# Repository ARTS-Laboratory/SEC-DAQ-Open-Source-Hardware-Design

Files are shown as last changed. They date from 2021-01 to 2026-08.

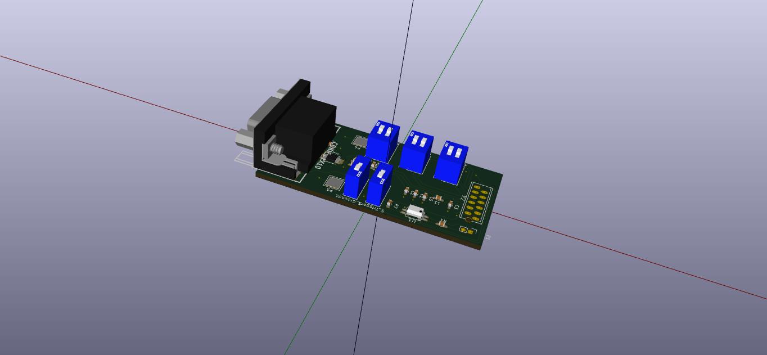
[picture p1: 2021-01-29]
versions/v0.9.2/hardware/KiCad_files/PCB layout/prototype.jpg

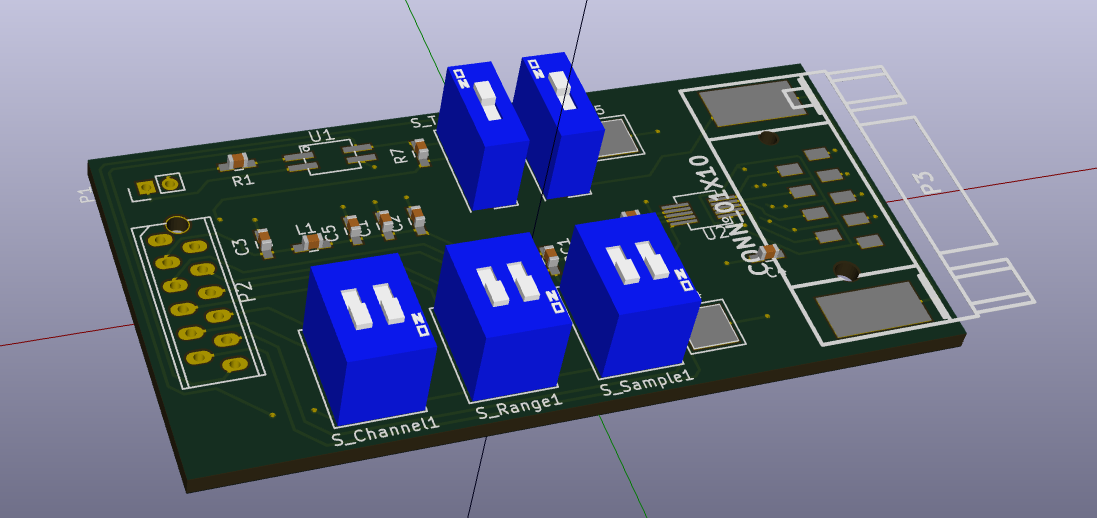
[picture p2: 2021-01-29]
versions/v0.9.2/hardware/KiCad_files/PCB layout/Selection_011.png

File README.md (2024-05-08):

# SEC DAQ
A 4-channel, 100 pF capacitance DAQ with active shielding designed for use with the Soft Elastomeric Capacitor (SEC) sensors but could be used for anything. 

<p align="center">

</p>

This data acquisition can measure SECs in the range of 15-115 pF, with an asynchronous sampling speed of 400 S/s on a single channel.

This hardware was used in various papers, including:
1. Downey, Austin, Anna Laura Pisello, Elena Fortunati, Claudia Fabiani, Francesca Luzi, Luigi Torre, Filippo Ubertini, and Simon Laflamme. "Durability and weatherability of a styrene-ethylene-butylene-styrene (SEBS) block copolymer-based sensing skin for civil infrastructure applications." Sensors and Actuators A: Physical 293 (2019): 269-280.
1. Downey, Austin, Mohammadkazem Sadoughi, Simon Laflamme, and Chao Hu. "Fusion of sensor geometry into additive strain fields measured with sensing skin." Smart Materials and Structures 27, no. 7 (2018): 075033.
1. Yan, Jin, Austin Downey, Alessandro Cancelli, Simon Laflamme, An Chen, Jian Li, and Filippo Ubertini. "Concrete crack detection and monitoring using a capacitive dense sensor array." Sensors 19, no. 8 (2019): 1843.

## Hardware design notes

### v0.9.0
1. Contains all the older files. 
1. Contains the 2-board PCB design

### v0.9.1
1. This is stable release. 
1. A 4-channel SEC DAC with isolated signal

### v0.9.2 (future version)
Improvements needed

#### High importance
1. The files needs to be cleaned up, and put back into a single KiCad file.
1. Compress the board layout so the DAQ sits inside the Arduino shield. (Reduces the wasted space)
1. Remove the ground tabs as adding a shield is a further work outside of these single box DAQs
1. Use a lower current draw opotcoupler, I think a CPC1301 should work. 
 
#### Medium importance
1. Move trigger housing into the board so it does not hang over.
1. Change the surface mount D-sub to a edge mount D-sub with signal/shield on top and ground on bottom. 
1. Add a switch for the time stamp so the DAQ only returns a time stamp if the switch in enabled. Will require a 14 pin IDC connector.

#### Low importance 
1. Enlarge the CDC filter capacitor solder pads
1. Add LED to the trigger circuit to help with trouble shooting (check current draw problems)

## Licensing and Citation

[][cc-by-sa]

This work is licensed under a
[Creative Commons Attribution-ShareAlike 4.0 International License][cc-by-sa].

[cc-by-sa]: http://creativecommons.org/licenses/by-sa/4.0/
[cc-by-sa-image]: https://licensebuttons.net/l/by-sa/4.0/88x31.png
[cc-by-sa-shield]: https://img.shields.io/badge/License-CC%20BY--SA%204.0-lightgrey.svg

Cite as:

@Misc{DowneySECDAQ,   
  author       = {Austin Downey},   
  howpublished = {GitHub},  
  title        = {{SEC} {DAQ} Open Source Hardware Design},   
  groups       = {{ARTS-L}ab},  
  url          = {https://github.com/ARTS-Laboratory/SEC-DAQ-Open-Source-Hardware-Design},  
}

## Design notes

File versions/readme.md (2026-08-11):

# Versions

## v0.9.0
The oldest source file we have, copeid and pasted with no changes. 

## v0.9.1 
A cleaned up and orginized version of v0.9.0. 

## v0.9.2
KiCAD files brought up to  Kicad v9.0.5 that can be found here https://downloads.kicad.org/kicad/windows/explore/stable 

## v0.10.0
An updated version of v0.9.2 that replaced the Uno with a nano and places it all on one PCB board

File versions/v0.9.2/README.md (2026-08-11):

# V0.9.2

## Hardware
PCB EDA files.

## Software
Arudino and LabVIEW source code.

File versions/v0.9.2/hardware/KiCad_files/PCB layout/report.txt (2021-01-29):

Info: Reading netlist file "/home/downey/Documents/IESS/Data_logger/Single_board_DAQ/v0.1/prototype.net".

Info: Using references to match components and footprints.

Info: Checking netlist component footprint "C1:/57FAB003:Capacitors_SMD:C_0603_HandSoldering".

Adding new component "C1:/57FAB003" footprint "Capacitors_SMD:C_0603_HandSoldering".

Changing component "C1:/57FAB003" pin "1" net name from "" to "+3V3".

Changing component "C1:/57FAB003" pin "2" net name from "" to "GNDA".

Info: Checking netlist component footprint "C2:/57FAB325:Capacitors_SMD:C_0603_HandSoldering".

Adding new component "C2:/57FAB325" footprint "Capacitors_SMD:C_0603_HandSoldering".

Changing component "C2:/57FAB325" pin "1" net name from "" to "+3V3".

Changing component "C2:/57FAB325" pin "2" net name from "" to "GNDA".

Info: Checking netlist component footprint "C3:/57FA96A1:Capacitors_SMD:C_0603_HandSoldering".

Adding new component "C3:/57FA96A1" footprint "Capacitors_SMD:C_0603_HandSoldering".

Changing component "C3:/57FA96A1" pin "1" net name from "" to "+3V3".

Changing component "C3:/57FA96A1" pin "2" net name from "" to "GNDA".

Info: Checking netlist component footprint "C4:/57FABCA3:Capacitors_SMD:C_0603_HandSoldering".

Adding new component "C4:/57FABCA3" footprint "Capacitors_SMD:C_0603_HandSoldering".

Changing component "C4:/57FABCA3" pin "1" net name from "" to "Net-(C4-Pad1)".

Changing component "C4:/57FABCA3" pin "2" net name from "" to "GNDA".

Info: Checking netlist component footprint "C5:/57FA9701:Capacitors_SMD:C_0603_HandSoldering".

Adding new component "C5:/57FA9701" footprint "Capacitors_SMD:C_0603_HandSoldering".

Changing component "C5:/57FA9701" pin "1" net name from "" to "+3V3".

Changing component "C5:/57FA9701" pin "2" net name from "" to "GNDA".

Info: Checking netlist component footprint "C6:/57FA977B:Capacitors_SMD:C_0603_HandSoldering".

Adding new component "C6:/57FA977B" footprint "Capacitors_SMD:C_0603_HandSoldering".

Changing component "C6:/57FA977B" pin "1" net name from "" to "+3V3".

Changing component "C6:/57FA977B" pin "2" net name from "" to "GNDA".

Info: Checking netlist component footprint "C7:/57FA97DE:Capacitors_SMD:C_0603_HandSoldering".

Adding new component "C7:/57FA97DE" footprint "Capacitors_SMD:C_0603_HandSoldering".

Changing component "C7:/57FA97DE" pin "1" net name from "" to "+3V3".

Changing component "C7:/57FA97DE" pin "2" net name from "" to "GNDA".

Info: Checking netlist component footprint "L1:/57FA9608:Capacitors_SMD:C_0603_HandSoldering".

Adding new component "L1:/57FA9608" footprint "Capacitors_SMD:C_0603_HandSoldering".

Changing component "L1:/57FA9608" pin "1" net name from "" to "+3V3".

Changing component "L1:/57FA9608" pin "2" net name from "" to "+3V3".

Info: Checking netlist component footprint "P1:/57FA0621:Pin_Headers:Pin_Header_Straight_1x02_Pitch2.00mm".

Adding new component "P1:/57FA0621" footprint "Pin_Headers:Pin_Header_Straight_1x02_Pitch2.00mm".

Changing component "P1:/57FA0621" pin "1" net name from "" to "Net-(P1-Pad1)".

Changing component "P1:/57FA0621" pin "2" net name from "" to "Net-(P1-Pad2)".

Info: Checking netlist component footprint "P2:/57F9FFFE:Downey:3M_12POS_ribbon_conn".

Adding new component "P2:/57F9FFFE" footprint "Downey:3M_12POS_ribbon_conn".

Changing component "P2:/57F9FFFE" pin "1" net name from "" to "GNDA".

Changing component "P2:/57F9FFFE" pin "2" net name from "" to "+5V".

Changing component "P2:/57F9FFFE" pin "3" net name from "" to "+3V3".

Changing component "P2:/57F9FFFE" pin "4" net name from "" to "SDA".

Changing component "P2:/57F9FFFE" pin "5" net name from "" to "SCL".

Changing component "P2:/57F9FFFE" pin "6" net name from "" to "Net-(P2-Pad6)".

Changing component "P2:/57F9FFFE" pin "7" net name from "" to "Net-(P2-Pad7)".

Changing component "P2:/57F9FFFE" pin "8" net name from "" to "Net-(P2-Pad8)".

Changing component "P2:/57F9FFFE" pin "9" net name from "" to "Net-(P2-Pad9)".

Changing component "P2:/57F9FFFE" pin "10" net name from "" to "Net-(P2-Pad10)".

Changing component "P2:/57F9FFFE" pin "11" net name from "" to "Net-(P2-Pad11)".

Changing component "P2:/57F9FFFE" pin "12" net name from "" to "trigger".

Info: Checking netlist component footprint "P3:/57FA3DE5:Downey:SMD_DSUB_9_female".

Adding new component "P3:/57FA3DE5" footprint "Downey:SMD_DSUB_9_female".

Changing component "P3:/57FA3DE5" pin "10" net name from "" to "Net-(P3-Pad10)".

Changing component "P3:/57FA3DE5" pin "9" net name from "" to "Net-(C4-Pad1)".

Changing component "P3:/57FA3DE5" pin "8" net name from "" to "GNDA".

Changing component "P3:/57FA3DE5" pin "7" net name from "" to "Net-(P3-Pad7)".

Changing component "P3:/57FA3DE5" pin "6" net name from "" to "GNDA".

Changing component "P3:/57FA3DE5" pin "5" net name from "" to "Net-(P3-Pad5)".

Changing component "P3:/57FA3DE5" pin "4" net name from "" to "GNDA".

Changing component "P3:/57FA3DE5" pin "3" net name from "" to "Net-(P3-Pad3)".

Changing component "P3:/57FA3DE5" pin "2" net name from "" to "GNDA".

Changing component "P3:/57FA3DE5" pin "1" net name from "" to "Net-(P3-Pad1)".

Changing component "P3:/57FA3DE5" pin "10" net name from "" to "Net-(P3-Pad10)".

Info: Checking netlist component footprint "R1:/57FA0735:Capacitors_SMD:C_0603_HandSoldering".

Adding new component "R1:/57FA0735" footprint "Capacitors_SMD:C_0603_HandSoldering".

Changing component "R1:/57FA0735" pin "1" net name from "" to "Net-(R1-Pad1)".

Changing component "R1:/57FA0735" pin "2" net name from "" to "Net-(P1-Pad2)".

Info: Checking netlist component footprint "R2:/57FA222C:Capacitors_SMD:C_0603_HandSoldering".

Adding new component "R2:/57FA222C" footprint "Capacitors_SMD:C_0603_HandSoldering".

Changing component "R2:/57FA222C" pin "1" net name from "" to "Net-(P2-Pad11)".

Changing component "R2:/57FA222C" pin "2" net name from "" to "GNDA".

Info: Checking netlist component footprint "R3:/57FA2141:Capacitors_SMD:C_0603_HandSoldering".

Adding new component "R3:/57FA2141" footprint "Capacitors_SMD:C_0603_HandSoldering".

Changing component "R3:/57FA2141" pin "1" net name from "" to "Net-(P2-Pad10)".

Changing component "R3:/57FA2141" pin "2" net name from "" to "GNDA".

Info: Checking netlist component footprint "R4:/57FA20F1:Capacitors_SMD:C_0603_HandSoldering".

Adding new component "R4:/57FA20F1" footprint "Capacitors_SMD:C_0603_HandSoldering".

Changing component "R4:/57FA20F1" pin "1" net name from "" to "Net-(P2-Pad9)".

Changing component "R4:/57FA20F1" pin "2" net name from "" to "GNDA".

Info: Checking netlist component footprint "R5:/57FA20A4:Capacitors_SMD:C_0603_HandSoldering".

Adding new component "R5:/57FA20A4" footprint "Capacitors_SMD:C_0603_HandSoldering".

Changing component "R5:/57FA20A4" pin "1" net name from "" to "Net-(P2-Pad8)".

Changing component "R5:/57FA20A4" pin "2" net name from "" to "GNDA".

Info: Checking netlist component footprint "R6:/57FA1675:Capacitors_SMD:C_0603_HandSoldering".

Adding new component "R6:/57FA1675" footprint "Capacitors_SMD:C_0603_HandSoldering".

Changing component "R6:/57FA1675" pin "1" net name from "" to "Net-(P2-Pad7)".

Changing component "R6:/57FA1675" pin "2" net name from "" to "GNDA".

Info: Checking netlist component footprint "R7:/57FA0A56:Capacitors_SMD:C_0603_HandSoldering".

Adding new component "R7:/57FA0A56" footprint "Capacitors_SMD:C_0603_HandSoldering".

Changing component "R7:/57FA0A56" pin "1" net name from "" to "+5V".

Changing component "R7:/57FA0A56" pin "2" net name from "" to "trigger".

Info: Checking netlist component footprint "R8:/57FA16D4:Capacitors_SMD:C_0603_HandSoldering".

Adding new component "R8:/57FA16D4" footprint "Capacitors_SMD:C_0603_HandSoldering".

Changing component "R8:/57FA16D4" pin "1" net name from "" to "Net-(P2-Pad6)".

Changing component "R8:/57FA16D4" pin "2" net name from "" to "GNDA".

Info: Checking netlist component footprint "RI2C1:/57FA72A6:Capacitors_SMD:C_0603_HandSoldering".

Adding new component "RI2C1:/57FA72A6" footprint "Capacitors_SMD:C_0603_HandSoldering".

Changing component "RI2C1:/57FA72A6" pin "1" net name from "" to "+3V3".

Changing component "RI2C1:/57FA72A6" pin "2" net name from "" to "SDA".

Info: Checking netlist component footprint "RI2C2:/57FA7321:Capacitors_SMD:C_0603_HandSoldering".

Adding new component "RI2C2:/57FA7321" footprint "Capacitors_SMD:C_0603_HandSoldering".

Changing component "RI2C2:/57FA7321" pin "1" net name from "" to "+3V3".

Changing component "RI2C2:/57FA7321" pin "2" net name from "" to "SCL".

Info: Checking netlist component footprint "S_Channel1:/57FA1B0F:Housings_DIP:DIP-4_W7.62mm_LongPads".

Adding new component "S_Channel1:/57FA1B0F" footprint "Housings_DIP:DIP-4_W7.62mm_LongPads".

Changing component "S_Channel1:/57FA1B0F" pin "1" net name from "" to "Net-(P2-Pad9)".

Changing component "S_Channel1:/57FA1B0F" pin "2" net name from "" to "Net-(P2-Pad8)".

Changing component "S_Channel1:/57FA1B0F" pin "3" net name from "" to "+5V".

Changing component "S_Channel1:/57FA1B0F" pin "4" net name from "" to "+5V".

Info: Checking netlist component footprint "S_Ground1:/57FA3888:Buttons_Switches_ThroughHole:SW_DIP_x1_Slide".

Adding new component "S_Ground1:/57FA3888" footprint "Buttons_Switches_ThroughHole:SW_DIP_x1_Slide".

Changing component "S_Ground1:/57FA3888" pin "1" net name from "" to "Net-(P3-Pad10)".

Changing component "S_Ground1:/57FA3888" pin "2" net name from "" to "GNDA".

Info: Checking netlist component footprint "S_Range1:/57FA13E3:Housings_DIP:DIP-4_W7.62mm_LongPads".

Adding new component "S_Range1:/57FA13E3" footprint "Housings_DIP:DIP-4_W7.62mm_LongPads".

Changing component "S_Range1:/57FA13E3" pin "1" net name from "" to "Net-(P2-Pad7)".

Changing component "S_Range1:/57FA13E3" pin "2" net name from "" to "Net-(P2-Pad6)".

Changing component "S_Range1:/57FA13E3" pin "3" net name from "" to "+5V".

Changing component "S_Range1:/57FA13E3" pin "4" net name from "" to "+5V".

Info: Checking netlist component footprint "S_Sample1:/57FA1BAD:Housings_DIP:DIP-4_W7.62mm_LongPads".

Adding new component "S_Sample1:/57FA1BAD" footprint "Housings_DIP:DIP-4_W7.62mm_LongPads".

Changing component "S_Sample1:/57FA1BAD" pin "1" net name from "" to "Net-(P2-Pad11)".

Changing component "S_Sample1:/57FA1BAD" pin "2" net name from "" to "Net-(P2-Pad10)".

Changing component "S_Sample1:/57FA1BAD" pin "3" net name from "" to "+5V".

Changing component "S_Sample1:/57FA1BAD" pin "4" net name from "" to "+5V".

Info: Checking netlist component footprint "S_Trigger1:/57FA3B05:Buttons_Switches_ThroughHole:SW_DIP_x1_Slide".

Adding new component "S_Trigger1:/57FA3B05" footprint "Buttons_Switches_ThroughHole:SW_DIP_x1_Slide".

Changing component "S_Trigger1:/57FA3B05" pin "1" net name from "" to "GNDA".

Changing component "S_Trigger1:/57FA3B05" pin "2" net name from "" to "trigger".

Info: Checking netlist component footprint "U1:/57FAE758:Downey:EL3H7".

Adding new component "U1:/57FAE758" footprint "Downey:EL3H7".

Changing component "U1:/57FAE758" pin "4" net name from "" to "trigger".

Changing component "U1:/57FAE758" pin "1" net name from "" to "Net-(R1-Pad1)".

Changing component "U1:/57FAE758" pin "3" net name from "" to "GNDA".

Changing component "U1:/57FAE758" pin "2" net name from "" to "Net-(P1-Pad1)".

Info: Checking netlist component footprint "U2:/57FA6132:Downey:SOIC_10_FDC1004".

Adding new component "U2:/57FA6132" footprint "Downey:SOIC_10_FDC1004".

Changing component "U2:/57FA6132" pin "10" net name from "" to "SDA".

Changing component "U2:/57FA6132" pin "1" net name from "" to "Net-(C4-Pad1)".

Changing component "U2:/57FA6132" pin "9" net name from "" to "SCL".

Changing component "U2:/57FA6132" pin "2" net name from "" to "Net-(P3-Pad1)".

Changing component "U2:/57FA6132" pin "8" net name from "" to "+3V3".

Changing component "U2:/57FA6132" pin "3" net name from "" to "Net-(P3-Pad3)".

Changing component "U2:/57FA6132" pin "7" net name from "" to "GNDA".

Changing component "U2:/57FA6132" pin "4" net name from "" to "Net-(P3-Pad5)".

Changing component "U2:/57FA6132" pin "6" net name from "" to "Net-(U2-Pad6)".

Changing component "U2:/57FA6132" pin "5" net name from "" to "Net-(P3-Pad7)".

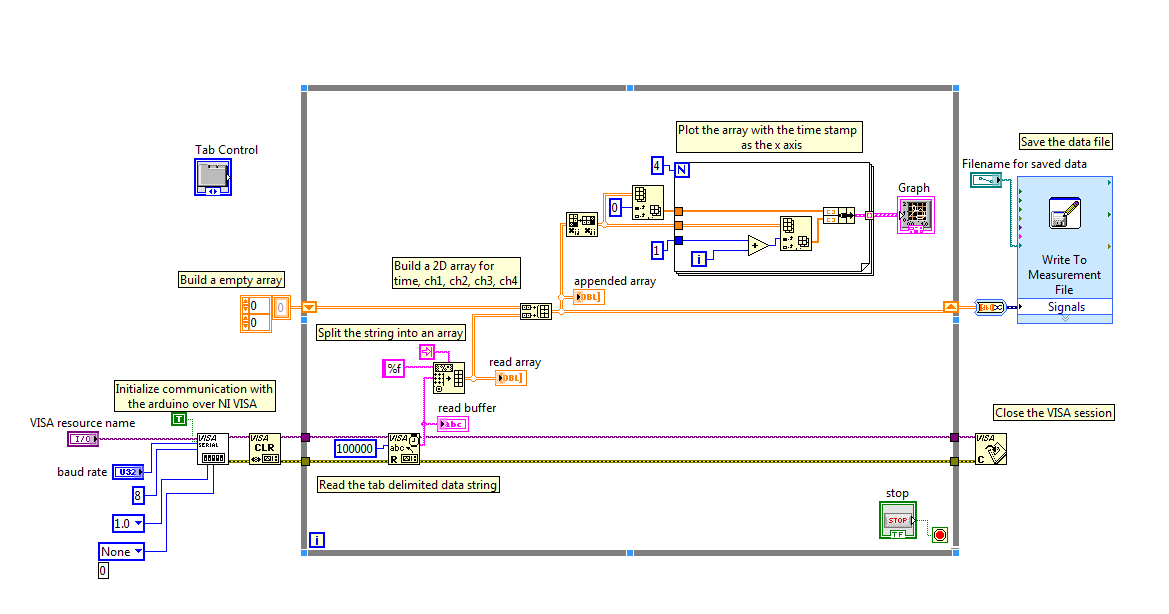
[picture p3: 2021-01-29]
versions/v0.9.2/software/LabView_code/Code.PNG

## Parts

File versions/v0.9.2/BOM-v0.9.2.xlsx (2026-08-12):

Internal Part Name | MFR / Vendor Description | MFR Part Number | Quantity | Individual Cost | Total Cost | Notes | Vendor 1 | Vendor 2 | Vendor 3 | Vendor 4
 | Cable equipment
CABLE TRIAXIAL RG-174 | HUBER+SUHNER | G_02332 | 3m | $11.82 | $35.55 | 3m continuous; cut into 2 × 1.5 m lengths | https://www.digikey.com/en/products/detail/huber-suhner-inc/G-02332/16806917
DB9 METAL BACKSHELL | Amphenol ICC (FCI) | 8655MH0901BLF | TBD | $6.47 | TBD | order qty as needed; Two-piece backshell; includes assembly hardware, grommets & 4-40 mating screws | https://www.digikey.com/en/products/detail/amphenol-cs-fci/8655MH0901BLF/1851324
DB9 MALE CONNECTOR | NorComp Inc | 171-009-103L001 | TBD | $1.29 | TBD | order qty as needed; 9-pin male D-sub connector | https://www.digikey.com/en/products/detail/norcomp-inc/171-009-103L001/858099?s=N4IgTCBcDaIIwHY4FoAMqCcy6oMwBl04QBdAXyA
J-B WELD ORIGINAL EPOXY | J-B Weld | 8265-S | 1 | $9.64 | $9.64 | Original Cold-Weld; steel-reinforced, 2-part epoxy | https://www.grainger.com/product/J-B-WELD-Epoxy-Adhesive-Professional-2UV83?searchQuery=8265-S&searchBar=true&tier=Tier+6&s_e=false
 | PCB Parts
9-pin d'sub female | Amphenol ICC (Commercial Products) | L17SM209SB14T | TBD | $9.16 | TBD | order qty as needed | https://www.digikey.com/en/products/detail/amphenol-cs-commercial-products/L17SM209SB14T/3464955
CDC | Texas Instruments | FDC1004QDGSRQ1 | TBD | $4.64 | TBD |  | https://www.digikey.com/en/products/detail/texas-instruments/FDC1004QDGSRQ1/5343524?s=N4IgTCBcDaIGIBEDCBGADGgLARQQcQGUAlbFEAXQF8g
Ribbon connector | TE Connectivity AMP Connectors | 1-2178713-2 | TBD | $0.47 | TBD |  | https://www.digikey.com/en/products/detail/wee/1-2178713-2/24894754
Ribbon cable | 3M | HF365/12SF | TBD | $2.54 | TBD |  | https://www.digikey.com/en/products/detail/3m/HF365-12SF/8256365
DIP 1 pos switch | Aratas (Formerly Omron Components) | A6TN-1104 | TBD | $1.23 | TBD |  | https://www.digikey.com/en/products/detail/aratas-formerly-omron-components/A6TN-1104/2754763?s=N4IgTCBcDaIIIDYAqA5AtARgwBgCwB18QBdAXyA
DIP 2 pos switch | Aratas (Formerly Omron Components) | A6TN-2104 | TBD | $1.64 | TBD |  | https://www.digikey.com/en/products/detail/aratas-formerly-omron-components/A6TN-2104/2627369?s=N4IgTCBcDaIIIDYAqA5AtGAjABgCwgF0BfIA
Box | Bud Industries | CN-6704 | TBD | $14.10 | TBD |  | https://www.digikey.com/en/products/detail/bud-industries/CN-6704/1219189?s=N4IgTCBcDaIMIDkC0A2A7ABgCwgLoF8g
Optocoupler | Everlight Electronics Co Ltd | EL3H7(TA)-VG | TBD | $0.51 | TBD |  | https://www.digikey.com/en/products/detail/everlight-electronics-co-ltd/EL3H7-TA-VG/2675689?s=N4IgTCBcDaIKIBkDMAJA7ACgCoEECUAtAGoDiIAugL5A
 | Capacitors
0.1 uF | CAP CER 0.1UF 25V X8R 0603 | C1608X8R1E104M080AA | TBD | $0.13 | TBD |  | https://www.digikey.com/en/products/detail/tdk/C1608X8R1E104M080AA/3951498
1 uF | CAP CER 1UF 10V X7R 0603 | C1608X7R1A105K080AC | TBD | $0.11 | TBD |  | https://www.digikey.com/en/products/detail/tdk/C1608X7R1A105K080AC/2093406
0.1 uF | CAP CER 0.1UF 25V X8R 0603 | C1608X8R1E104K080AA | TBD | $0.13 | TBD |  | https://www.digikey.com/en/products/detail/tdk/C1608X8R1E104K080AA/927126
51 uF | CAP CER 51PF 50V C0G/NP0 0603 | CL10C510JB8NNNC | TBD | $0.10 | TBD |  | https://www.digikey.com/en/products/detail/samsung-electro-mechanics/CL10C510JB8NNNC/3887968
 | Resistors
0k1 | RES SMD 100 OHM 1% 1/10W 0603 | AC0603FR-07100RL | TBD | $0.10 | TBD |  | https://www.digikey.com/en/products/detail/yageo/AC0603FR-07100RL/5895735
10k | RES SMD 10K OHM 5% 1/10W 0603 | AC0603JR-0710KL | TBD | $0.10 | TBD |  | https://www.digikey.com/en/products/detail/yageo/AC0603JR-0710KL/2827830
4k7 | RES SMD 4.7K OHM 5% 1/10W 0603 | AC0603JR-074K7L | TBD | $0.10 | TBD |  | https://www.digikey.com/en/products/detail/yageo/AC0603JR-074K7L/5896467

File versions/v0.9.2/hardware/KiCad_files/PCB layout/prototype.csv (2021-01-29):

Source | /home/downey/Documents/IESS/Data_logger/Single_board_DAQ/v0.1/prototype.sch
Kicad Rev | Eeschema 4.0.4+e1-6308~48~ubuntu14.04.1-stable
Generated Date | Sat 15 Oct 2016 10:10:26 AM CEST
Title | Single Board DAQ
Company | IESS
Revision | V0.1
Date Issue | 2016-10-15
Reference | Value | Library | Library Ref
P2 | CONN_01X12 | conn | CONN_01X12
P1 | CONN_01X02 | conn | CONN_01X02
R1 | 0k1 | device | R
R7 | 10k | device | R
S_Range1 | DIPS_02 | dips-s | DIPS_02
R6 | 10k | device | R
R8 | 10k | device | R
S_Channel1 | DIPS_02 | dips-s | DIPS_02
S_Sample1 | DIPS_02 | dips-s | DIPS_02
R5 | 10k | device | R
R4 | 10k | device | R
R3 | 10k | device | R
R2 | 10k | device | R
S_Ground1 | DIPS_01 | dips-s | DIPS_01
S_Trigger1 | DIPS_01 | dips-s | DIPS_01
P3 | CONN_01X10 | conn | CONN_01X10
U2 | FDC1004custom | Downey | FDC1004custom
RI2C1 | 4k7 | device | R
RI2C2 | 4k7 | device | R
L1 | 1uH | device | INDUCTOR
C3 | 100uF | device | C
C5 | 10uF | device | C
C6 | 1uF | device | C
C7 | 0.1uF | device | C
C1 | 1uF | device | C
C2 | 0.1uF | device | C
C4 | 51pF | device | C
U1 | EL3H7 | Downey | EL3H7
P5 | CONN_01X01 | conn | CONN_01X01
P4 | CONN_01X01 | conn | CONN_01X01

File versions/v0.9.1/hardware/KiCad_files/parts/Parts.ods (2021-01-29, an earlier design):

Part | Part number | needed | price | cost
9-pin d'sub female | L17SM209SB14T-ND | 1 | $5.64 | $5.64
CDC | 296-42334-1-ND | 1 | $8.32 | $8.32
Ribbon connector | A120912CT-ND | 1 | $0.96 | $0.96
Ribbon cable | MD12R-5-ND | 1 | $6.54 | $6.54
Panel-Mount USB 2.0 | B&H # CA28073 | 1 | $6.37 | $6.37
Back plane connector | A105201-ND | 1 | $8.16 | $8.16 | Back plane connector | 609-3129-ND | 1 | $2.92 | $2.92
9-pin d'sub male | 5-747904-5-ND | 1 | $2.78 | $2.78 | 9-pin d'sub male | L717SDE09P-ND | 1 | $0.69 | $0.69
DIP 1 pos switch | Z5195-ND | 2 | $0.85 | $1.70
DIP 2 pos switch | SW1198-ND | 3 | $0.88 | $2.64
Box | 377-1528-ND | 1 | $11.14 | $11.14
BNC trigger | ARFX1905-ND | 1 | $2.51 | $2.51
Optocoupler | 1080-1198-1-ND | 1 | $0.61 | $0.61
Stand offs |  | 2 | $1.00 | $2.00
Pcb boards | OshPark | 1 | $10.00 | $10.00 | per board
Capacitors
10 uF | 445-14262-1-ND | 10 | $0.10 | $1.00
1 uF | 445-5138-1-ND | 10 | $0.10 | $1.00
0.1 uF | 445-2500-1-ND | 10 | $0.10 | $1.00
51 uF | 1276-2310-1-ND | 10 | $0.10 | $1.00
Resistors
0k1 | YAG3561CT-ND | 10 | $0.10 | $1.00
10k | 311-10KLECT-ND | 10 | $0.10 | $1.00
4k7 | YAG3676CT-ND | 10 | $0.10 | $1.00
 |  |  |  | $0.00
 |  |  |  | $0.00
 |  |  | total | $76.37

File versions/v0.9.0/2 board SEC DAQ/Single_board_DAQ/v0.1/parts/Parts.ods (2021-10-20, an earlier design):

Part | Part number | needed | price | cost
9-pin d'sub female | A108289CT-ND | 1 | $8.40 | $8.40
CDC | 296-42334-1-ND | 1 | $8.32 | $8.32
DIP switch | CKN6055-ND | 2 | $0.94 | $1.88
Ribbon connector | A120912CT-ND | 1 | $0.96 | $0.96
Ribbon cable | MC14G-5-ND | 1 | $4.31 | $4.31
Type-B USB connector | MUSBD11130-ND | 1 | $9.58 | $9.58
Back plane connector | A105201-ND | 1 | $8.16 | $8.16
9-pin d'sub male | 5-747904-5-ND | 1 | $2.78 | $2.78
2.5 mm barrel plug | CP-066B-ND | 1 | $2.60 | $2.60
SPST switch | CKN10664-ND | 2 | $1.12 | $2.24
Box | 377-1527-ND | 1 | $11.11 | $11.11
BNC trigger | ARFX1905-ND | 1 | $2.51 | $2.51
Optocoupler | 1080-1198-1-ND | 1 | $0.61 | $0.61
Pcb boards | OshPark | 1 | $17.75 | $17.75
Capacitors
10 uF | 445-14262-1-ND | 10 | $0.10 | $1.00
1 uF | 445-5138-1-ND | 10 | $0.10 | $1.00
0.1 uF | 445-2500-1-ND | 10 | $0.10 | $1.00
51 uF | 1276-2310-1-ND | 10 | $0.10 | $1.00
100 uF | xxx |  |  | $0.00
Resistors |  |  |  | $0.00
0k1 | YAG3561CT-ND | 10 | $0.10 | $1.00
10k | 311-10KLECT-ND | 10 | $0.10 | $1.00
4k7 | YAG3676CT-ND | 10 | $0.10 | $1.00
 |  |  |  | $0.00
 |  |  |  | $0.00
 |  |  | total | $88.21

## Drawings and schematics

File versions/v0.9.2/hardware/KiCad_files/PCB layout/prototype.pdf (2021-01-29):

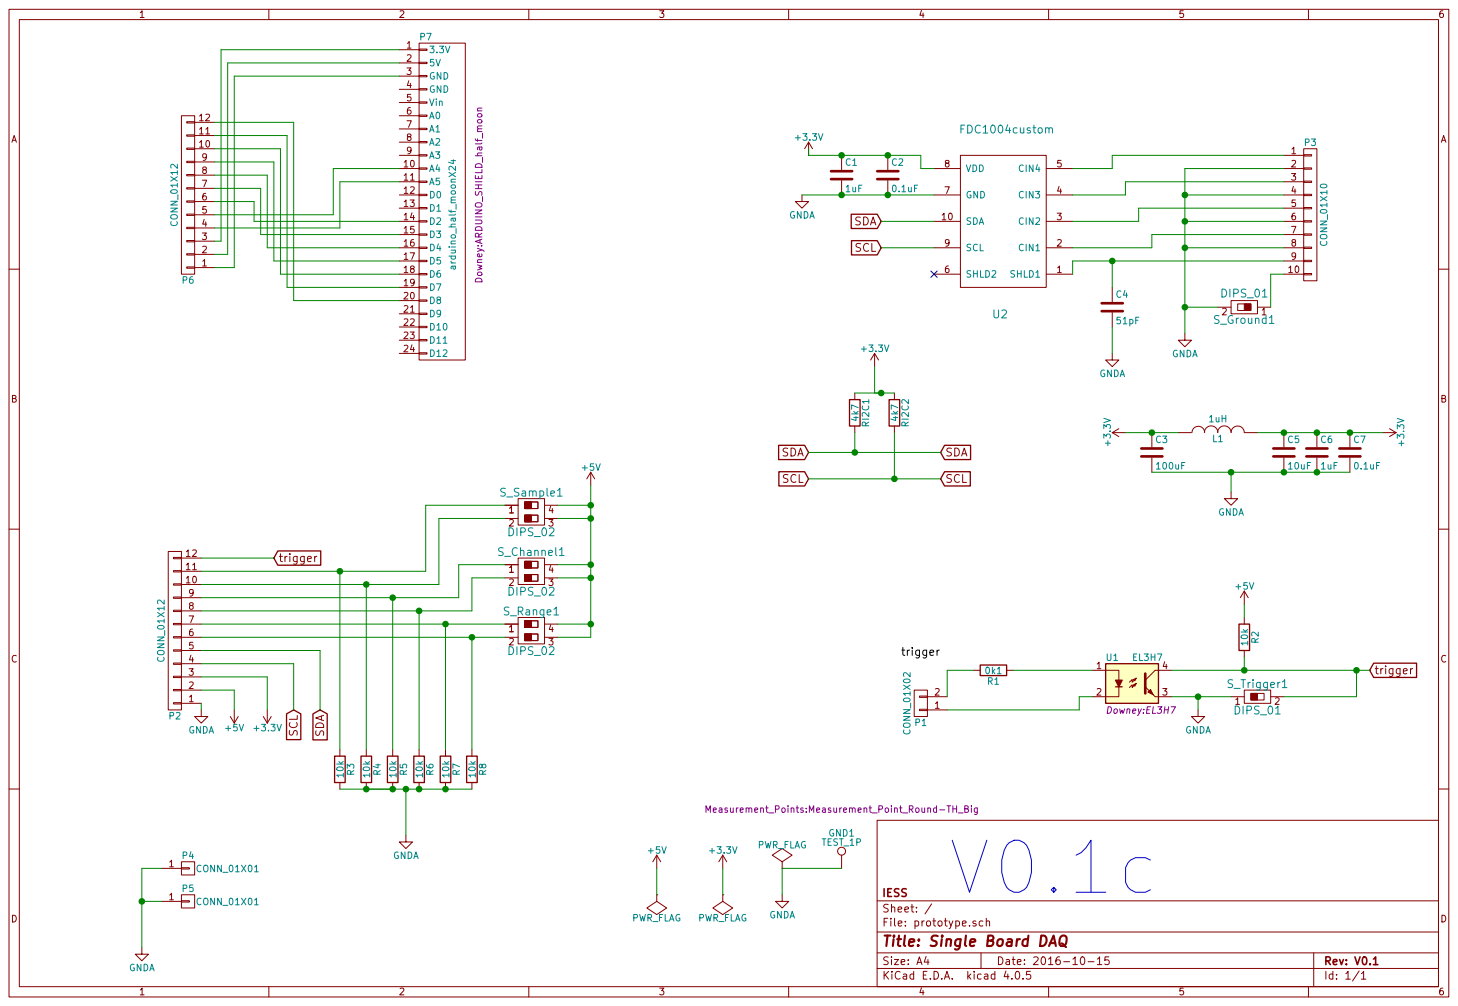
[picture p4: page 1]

File: prototype.sch Sheet: /
Id: 1/1 Title: Single Board DAQ

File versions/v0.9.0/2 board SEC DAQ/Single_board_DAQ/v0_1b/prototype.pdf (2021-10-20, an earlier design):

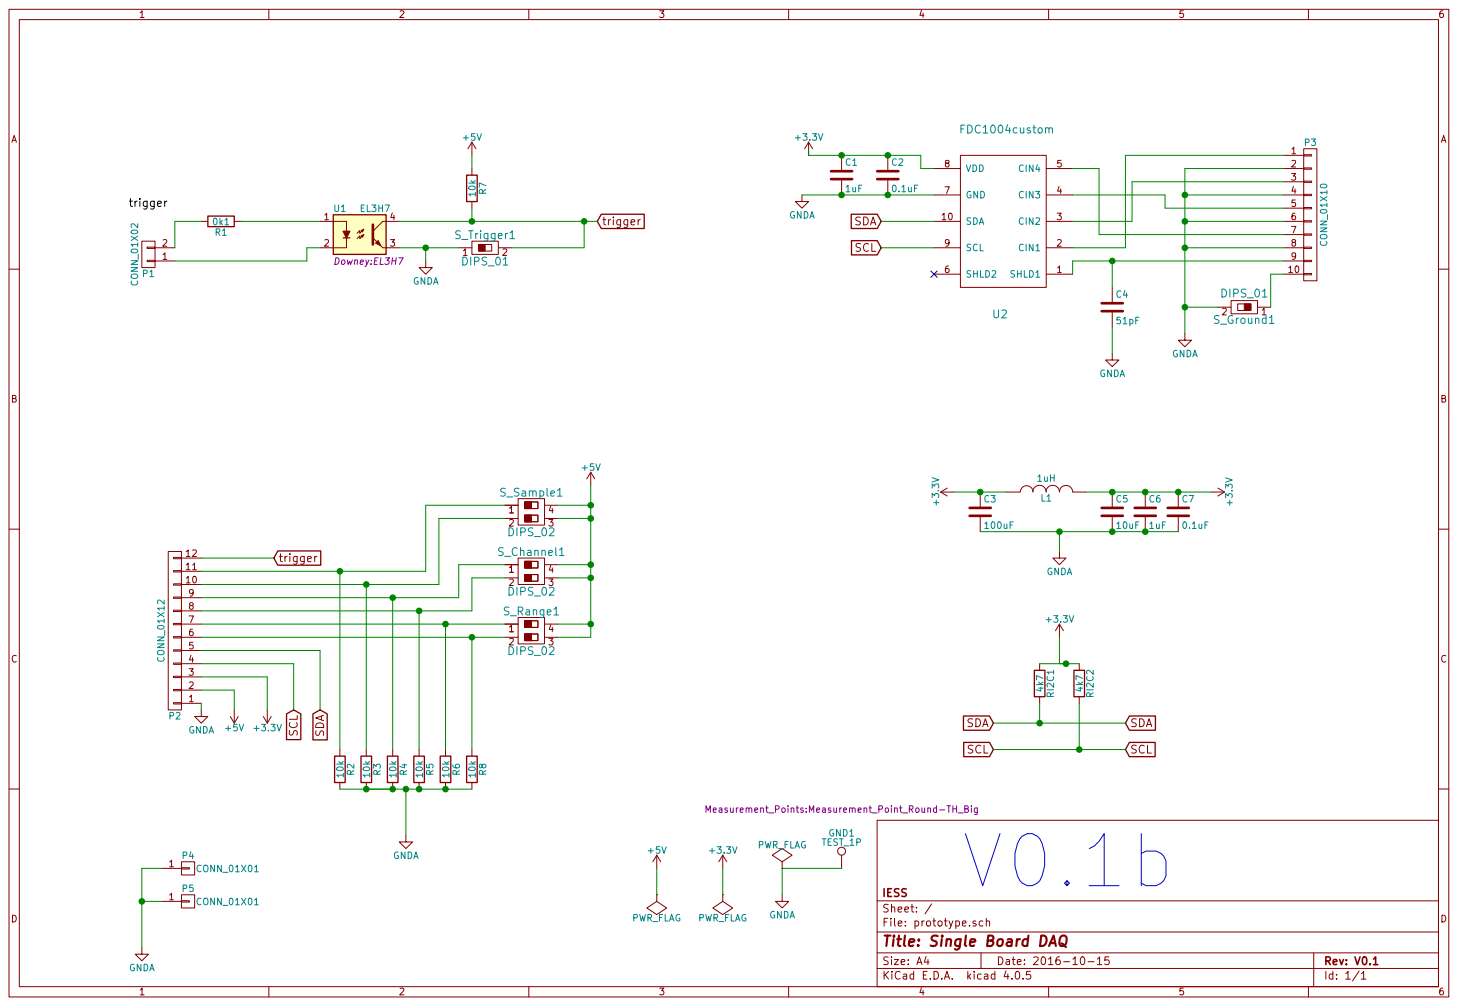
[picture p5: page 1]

IESS
File: prototype.sch Sheet: /
Id: 1/1 Title: Single Board DAQ

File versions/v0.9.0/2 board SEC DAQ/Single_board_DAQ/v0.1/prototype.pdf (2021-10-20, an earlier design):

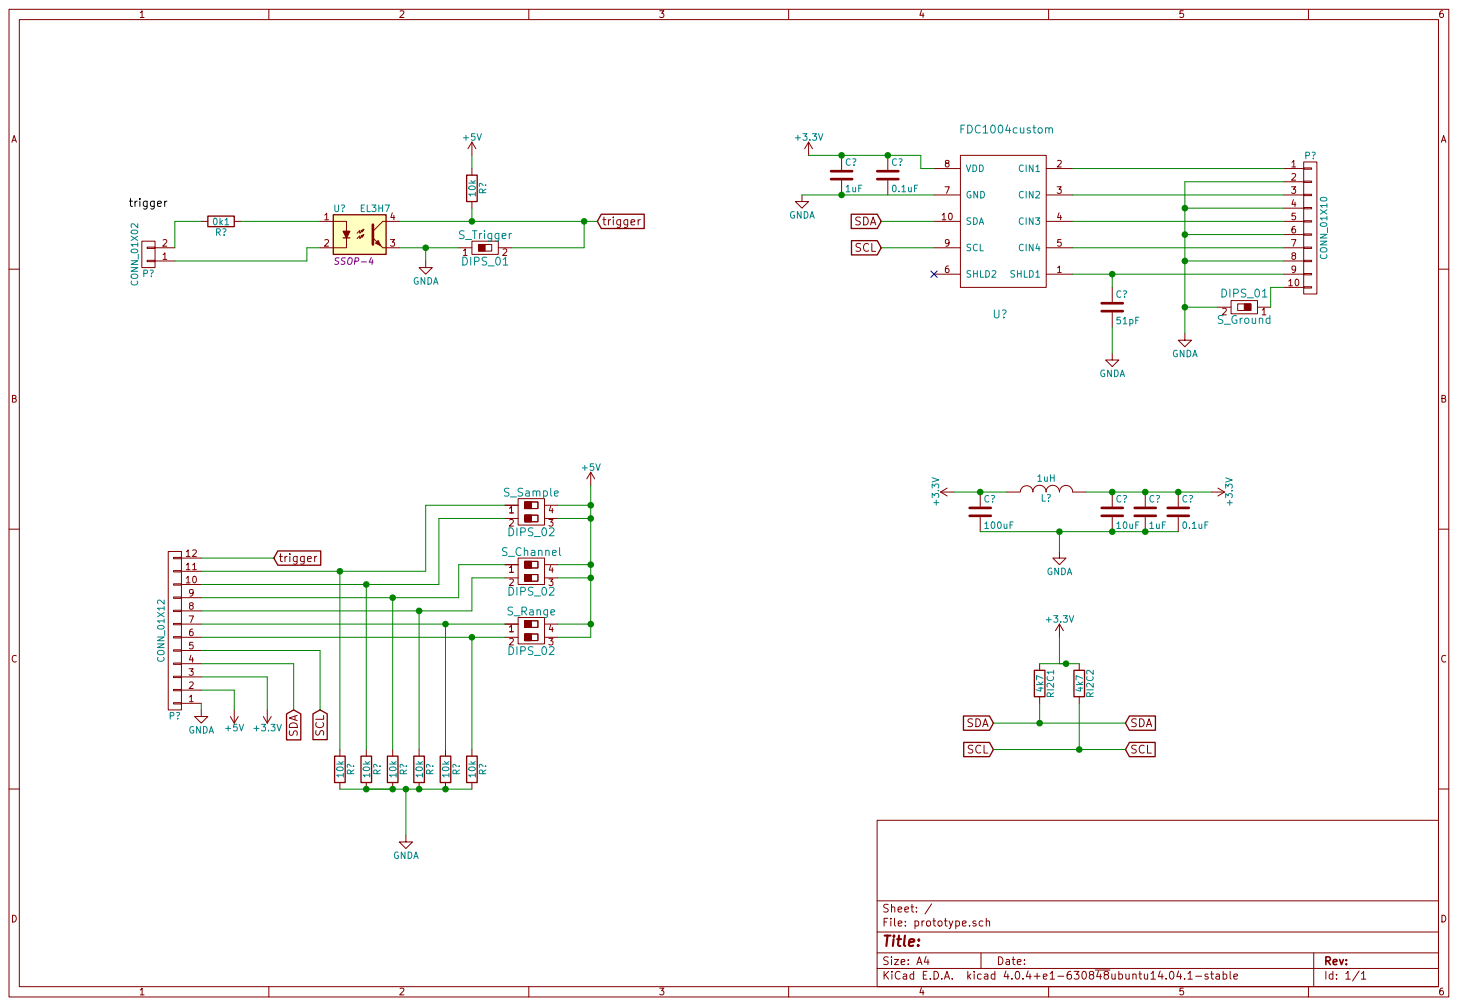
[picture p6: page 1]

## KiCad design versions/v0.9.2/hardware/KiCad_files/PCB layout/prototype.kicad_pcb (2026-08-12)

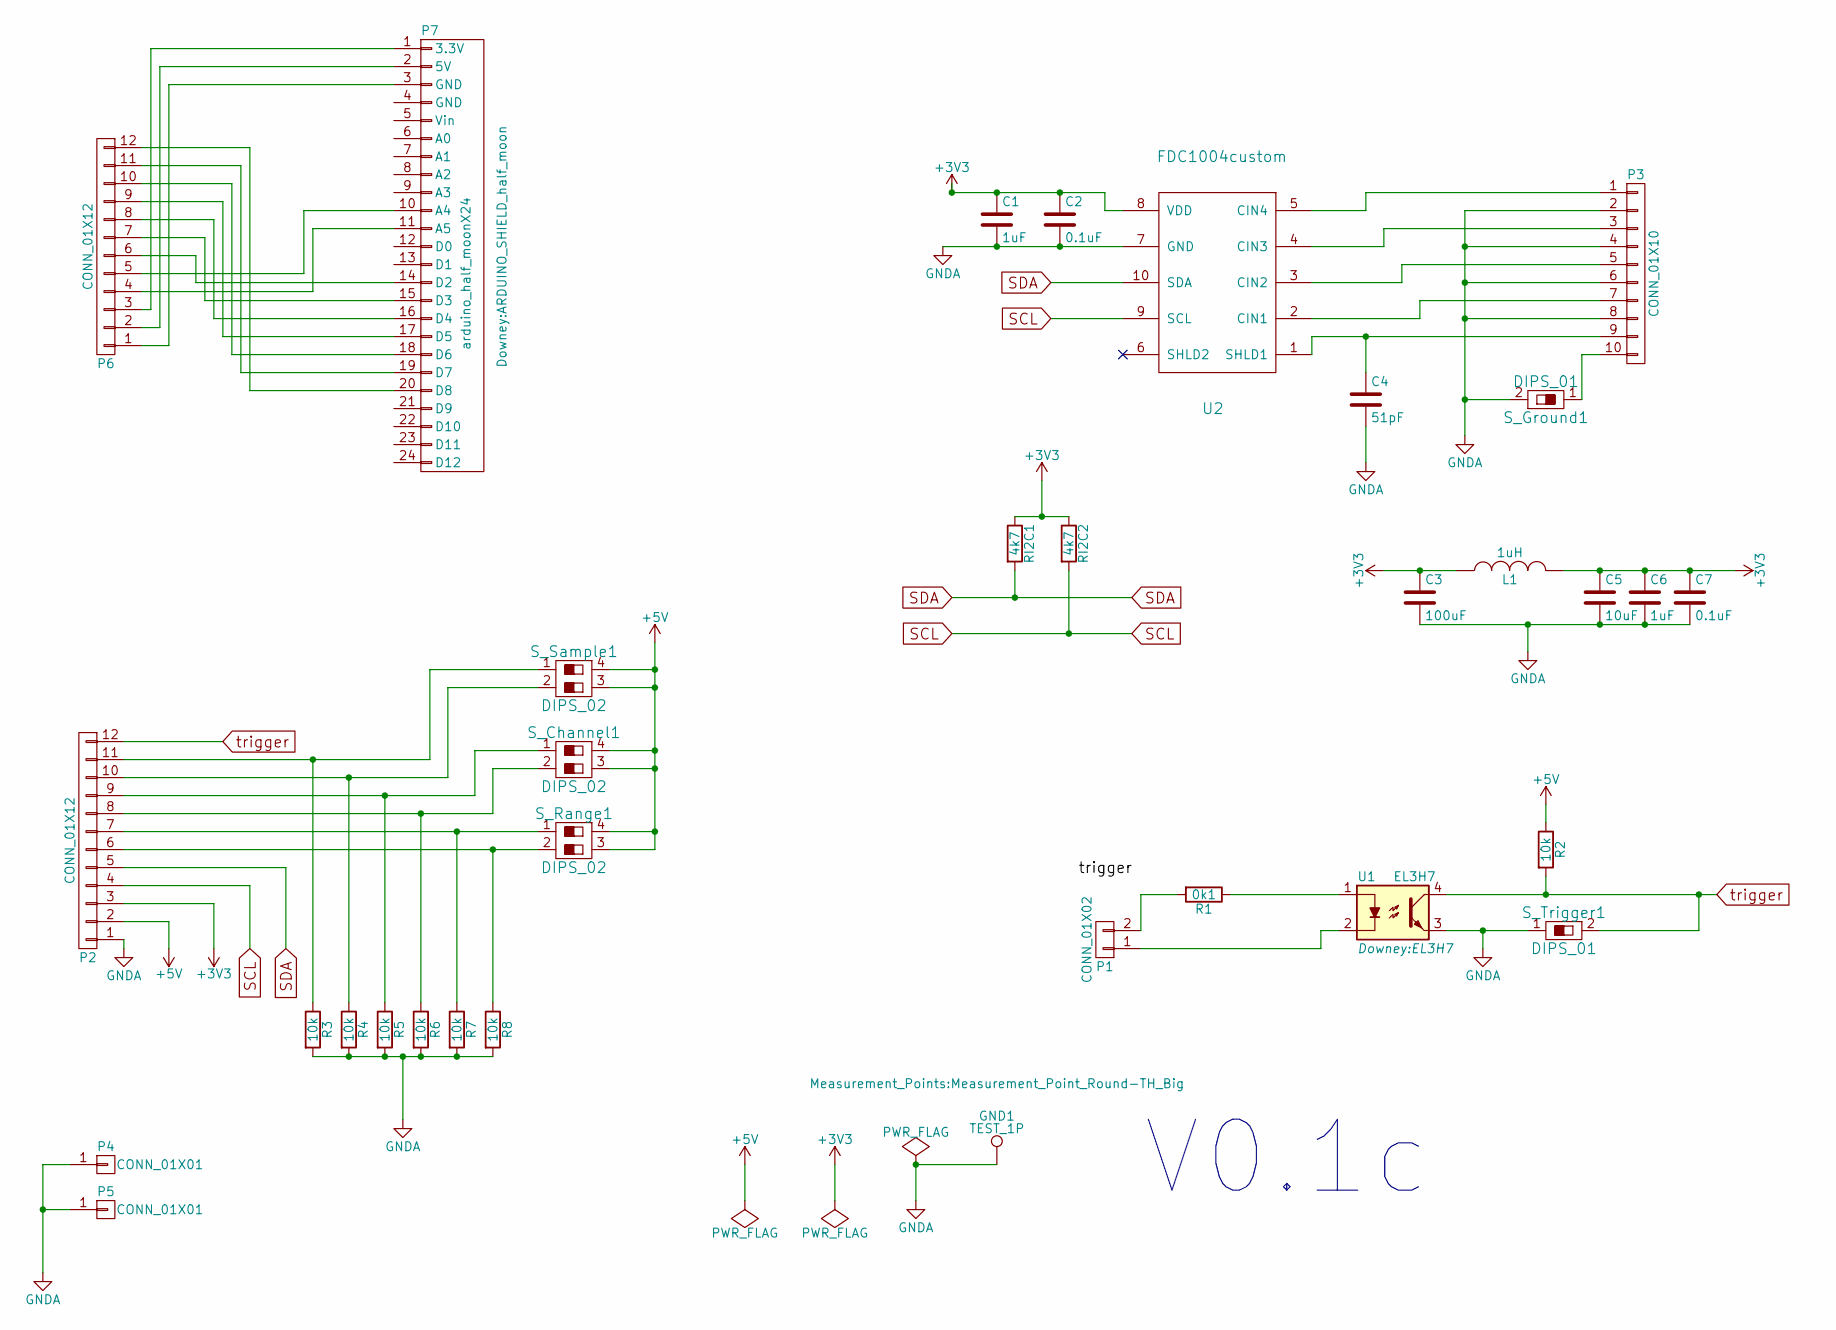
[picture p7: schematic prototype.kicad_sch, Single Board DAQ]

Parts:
C1, C6: 1uF; C_0805_HandSoldering
C2, C7: 0.1uF; C_0805_HandSoldering
C3: 100uF; C_1206_HandSoldering
C4: 51pF; C_0805_HandSoldering
C5: 10uF; C_0805_HandSoldering
GND1: TEST_1P; Measurement_Point_Round-TH_Big
L1: 1uH; R_0805_HandSoldering
P1: CONN_01X02; Pin_Header_Straight_1x02_Pitch2.00mm
P2, P6: CONN_01X12; 3M_12POS_ribbon_conn
P3: CONN_01X10; DSUB-9_surface_mount
P4, P5: CONN_01X01; 1Pin
P7: arduino_half_moonX24; ARDUINO_SHIELD_half_moon
R1: 0k1; R_1206_HandSoldering
R2, R3, R4, R5, R6, R7, R8: 10k; R_1206_HandSoldering
RI2C1, RI2C2: 4k7; R_1206_HandSoldering
S_Channel1: DIPS_02; SW_DIP_x2_W7.62mm_Slide
S_Ground1: DIPS_01; SW_DIP_x1_W7.62mm_Slide
S_Range1: DIPS_02; SW_DIP_x2_W7.62mm_Slide
S_Sample1: DIPS_02; SW_DIP_x2_W7.62mm_Slide
S_Trigger1: DIPS_01; SW_DIP_x1_W7.62mm_Slide
U1: EL3H7
U2: FDC1004custom; SOIC_10_FDC1004

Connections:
+3V3: C1.1, C2.1, C3.1, C5.1, C6.1, C7.1, L1.1, L1.2, P2.3, RI2C1.1, RI2C2.1, U2.8 (VDD)
+5V: P2.2, R2.1, S_Channel1.3, S_Channel1.4, S_Range1.3, S_Range1.4, S_Sample1.3, S_Sample1.4
GNDA: C1.2, C2.2, C3.2, C4.2, C5.2, C6.2, C7.2, GND1.1, P2.1, P3.2, P3.4, P3.6, P3.8, P4.1, P5.1, R3.2, R4.2, R5.2, R6.2, R7.2, R8.2, S_Ground1.2, S_Trigger1.1, U1.3, U2.7 (GND)
unnamed: C4.1, P3.9, U2.1 (SHLD1)
unnamed: P1.1, U1.2
unnamed: P1.2, R1.2
unnamed: P2.6, R8.1, S_Range1.2
unnamed: P2.7, R7.1, S_Range1.1
unnamed: P2.8, R6.1, S_Channel1.2
unnamed: P2.9, R5.1, S_Channel1.1
unnamed: P2.10, R4.1, S_Sample1.2
unnamed: P2.11, R3.1, S_Sample1.1
unnamed: P3.1, U2.5 (CIN4)
unnamed: P3.3, U2.4 (CIN3)
unnamed: P3.5, U2.3 (CIN2)
unnamed: P3.7, U2.2 (CIN1)
unnamed: P3.10, S_Ground1.1
unnamed: P6.1, P7.3 (GND)
unnamed: P6.2, P7.2 (5V)
unnamed: P6.3, P7.1 (3.3V)
unnamed: P6.4, P7.11 (A5)
unnamed: P6.5, P7.10 (A4)
unnamed: P6.6, P7.14 (D2)
unnamed: P6.7, P7.15 (D3)
unnamed: P6.8, P7.16 (D4)
unnamed: P6.9, P7.17 (D5)
unnamed: P6.10, P7.18 (D6)
unnamed: P6.11, P7.19 (D7)
unnamed: P6.12, P7.20 (D8)
unnamed: R1.1, U1.1
SCL: P2.4, RI2C2.2, U2.9 (SCL)
SDA: P2.5, RI2C1.2, U2.10 (SDA)
trigger: P2.12, R2.2, S_Trigger1.2, U1.4

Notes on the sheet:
V0.1c

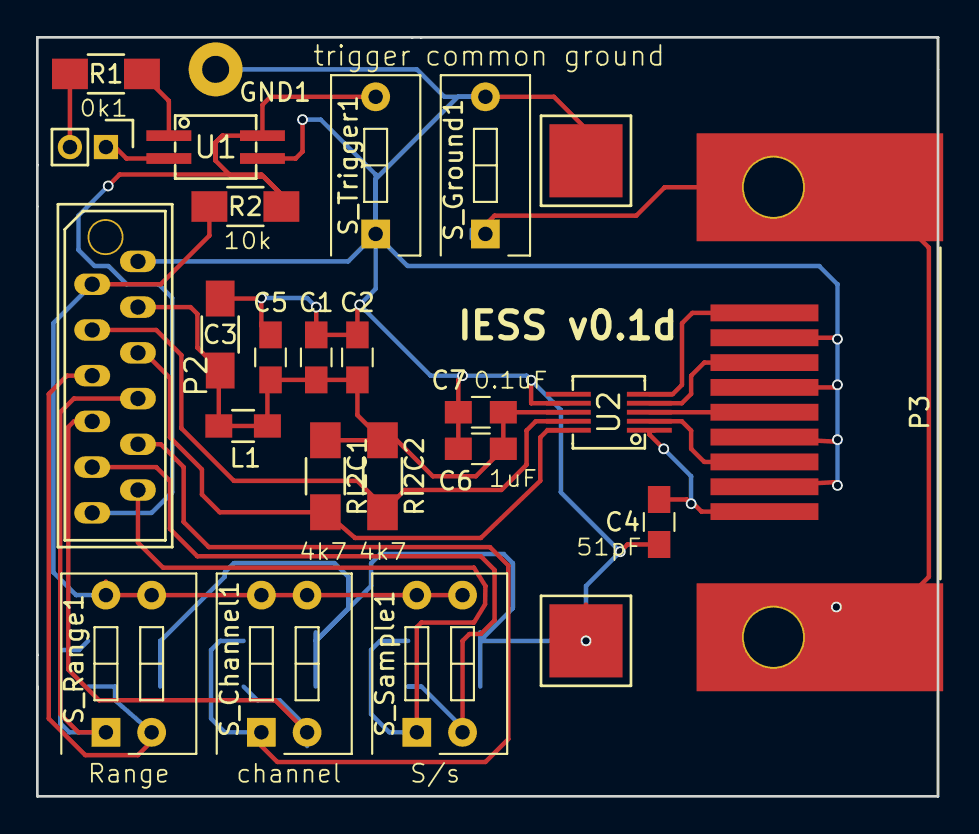
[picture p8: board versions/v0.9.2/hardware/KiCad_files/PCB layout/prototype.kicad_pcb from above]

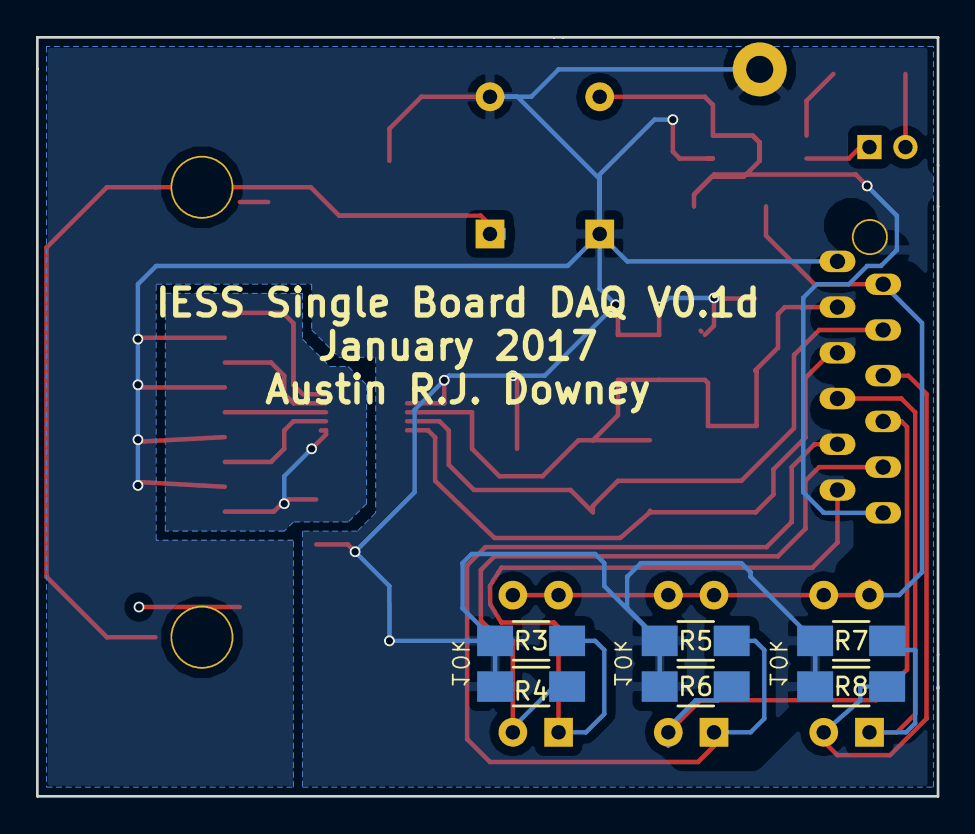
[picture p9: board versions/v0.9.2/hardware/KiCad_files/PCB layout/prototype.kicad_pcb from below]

Board: 2 copper layers, 50.0 x 42.2 mm, 31 parts (6 on the bottom side), 21 nets.

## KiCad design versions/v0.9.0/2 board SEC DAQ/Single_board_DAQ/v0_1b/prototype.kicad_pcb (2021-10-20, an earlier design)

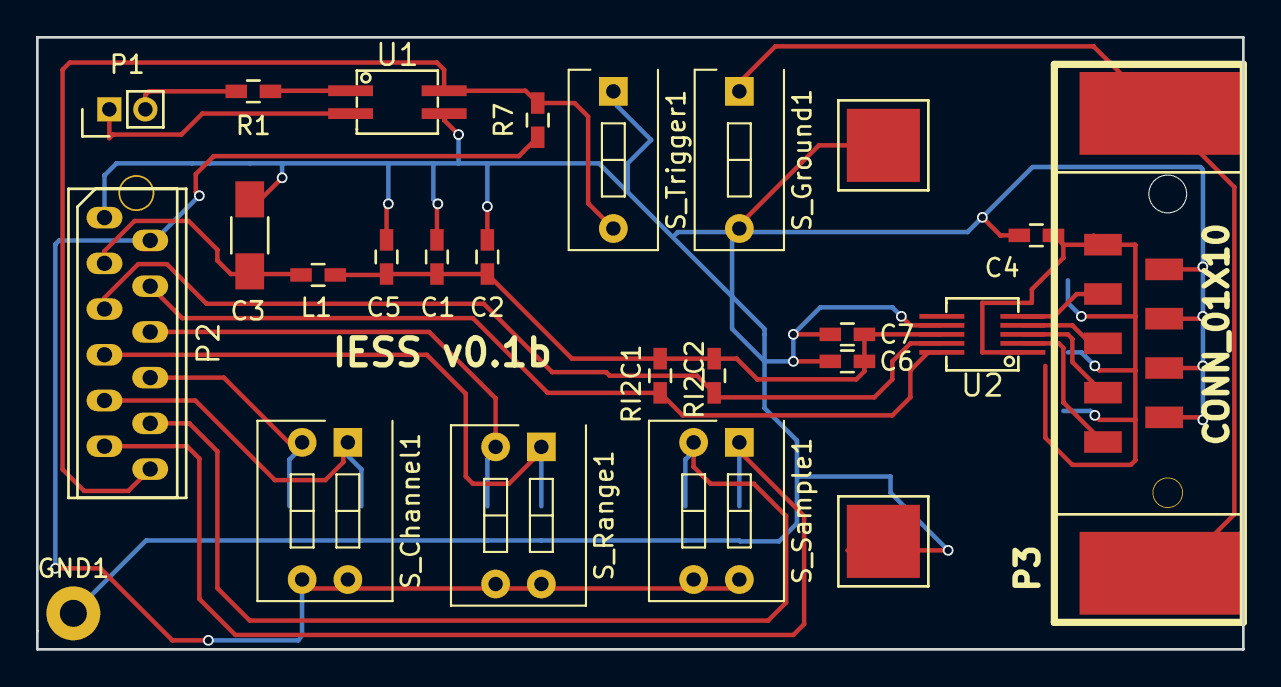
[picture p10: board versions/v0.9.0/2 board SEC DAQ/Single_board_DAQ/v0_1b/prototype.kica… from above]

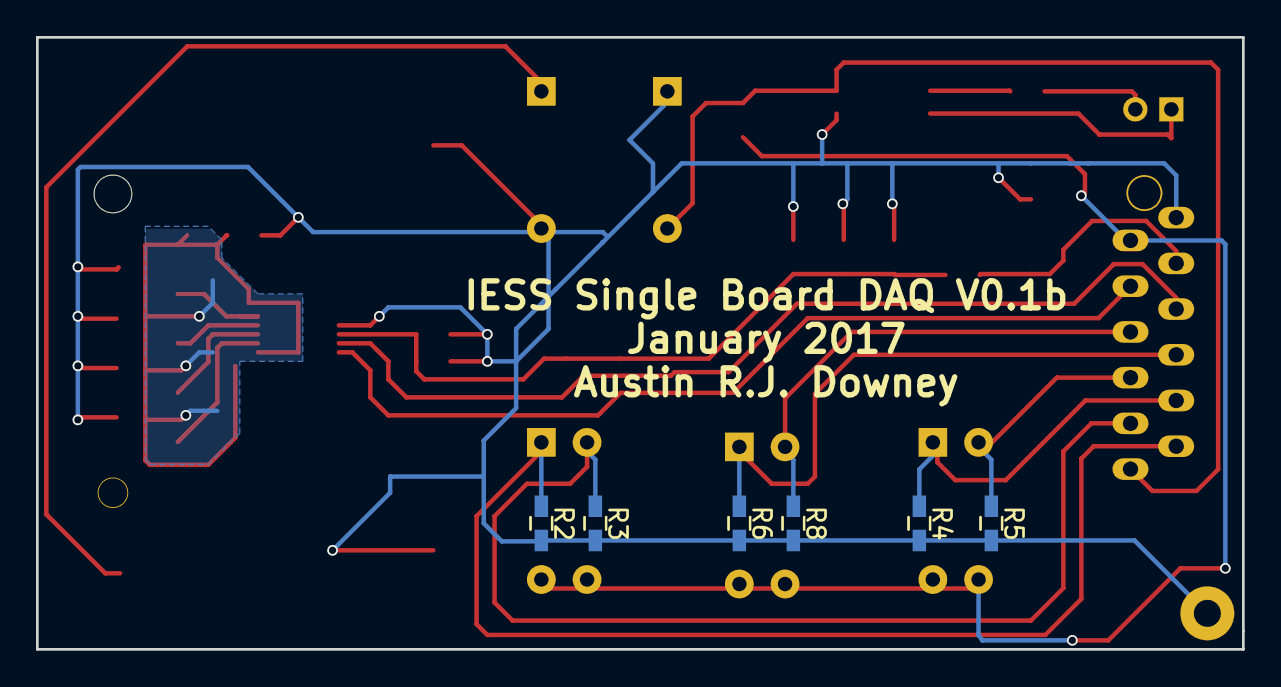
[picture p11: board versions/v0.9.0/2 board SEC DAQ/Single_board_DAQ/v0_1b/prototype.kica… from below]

Board: 2 copper layers, 67.0 x 34.0 mm, 31 parts (6 on the bottom side), 21 nets.

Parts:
C1, C6: 1uF; C_0603_HandSoldering
C2, C7: 0.1uF; C_0603_HandSoldering
C3: 100uF; C_1206_HandSoldering
C4: 51pF; C_0603_HandSoldering
C5: 10uF; C_0603_HandSoldering
GND1: TEST_1P; Measurement_Point_Round-TH_Big
L1: 1uH; C_0603_HandSoldering
P1: CONN_01X02; Pin_Header_Straight_1x02_Pitch2.00mm
P2: CONN_01X12; 3M_12POS_ribbon_conn
P3: CONN_01X10; SMD_DSUB_9_female
P4, P5: CONN_01X01; 1Pin
R1: 0k1; C_0603_HandSoldering
R2, R3, R4, R5, R6, R7, R8: 10k; C_0603_HandSoldering
RI2C1, RI2C2: 4k7; C_0603_HandSoldering
S_Channel1: DIPS_02; SW_DIP_x2_W7.62mm_Slide
S_Ground1: DIPS_01; SW_DIP_x1_W7.62mm_Slide
S_Range1: DIPS_02; SW_DIP_x2_W7.62mm_Slide
S_Sample1: DIPS_02; SW_DIP_x2_W7.62mm_Slide
S_Trigger1: DIPS_01; SW_DIP_x1_W7.62mm_Slide
U1: EL3H7
U2: FDC1004custom; SOIC_10_FDC1004

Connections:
+3V3: C1.1, C2.1, C3.1, C5.1, C6.1, C7.1, L1.1, L1.2, P2.3, RI2C1.1, RI2C2.1, U2.8
+5V: P2.2, R7.1, S_Channel1.3, S_Channel1.4, S_Range1.3, S_Range1.4, S_Sample1.3, S_Sample1.4
GNDA: C1.2, C2.2, C3.2, C4.2, C5.2, C6.2, C7.2, GND1.1, P2.1, P3.2, P3.4, P3.6, P3.8, P4.1, P5.1, R2.2, R3.2, R4.2, R5.2, R6.2, R8.2, S_Ground1.2, S_Trigger1.1, U1.3, U2.7
unnamed: C4.1, P3.9, U2.1
unnamed: P1.1, U1.2
unnamed: P1.2, R1.2
unnamed: P2.6, R8.1, S_Range1.2
unnamed: P2.7, R6.1, S_Range1.1
unnamed: P2.8, R5.1, S_Channel1.2
unnamed: P2.9, R4.1, S_Channel1.1
unnamed: P2.10, R3.1, S_Sample1.2
unnamed: P2.11, R2.1, S_Sample1.1
unnamed: P3.1, U2.2
unnamed: P3.3, U2.3
unnamed: P3.5, U2.4
unnamed: P3.7, U2.5
unnamed: P3.10, S_Ground1.1
unnamed: R1.1, U1.1
SCL: P2.5, RI2C2.2, U2.9
SDA: P2.4, RI2C1.2, U2.10
trigger: P2.12, R7.2, S_Trigger1.2, U1.4

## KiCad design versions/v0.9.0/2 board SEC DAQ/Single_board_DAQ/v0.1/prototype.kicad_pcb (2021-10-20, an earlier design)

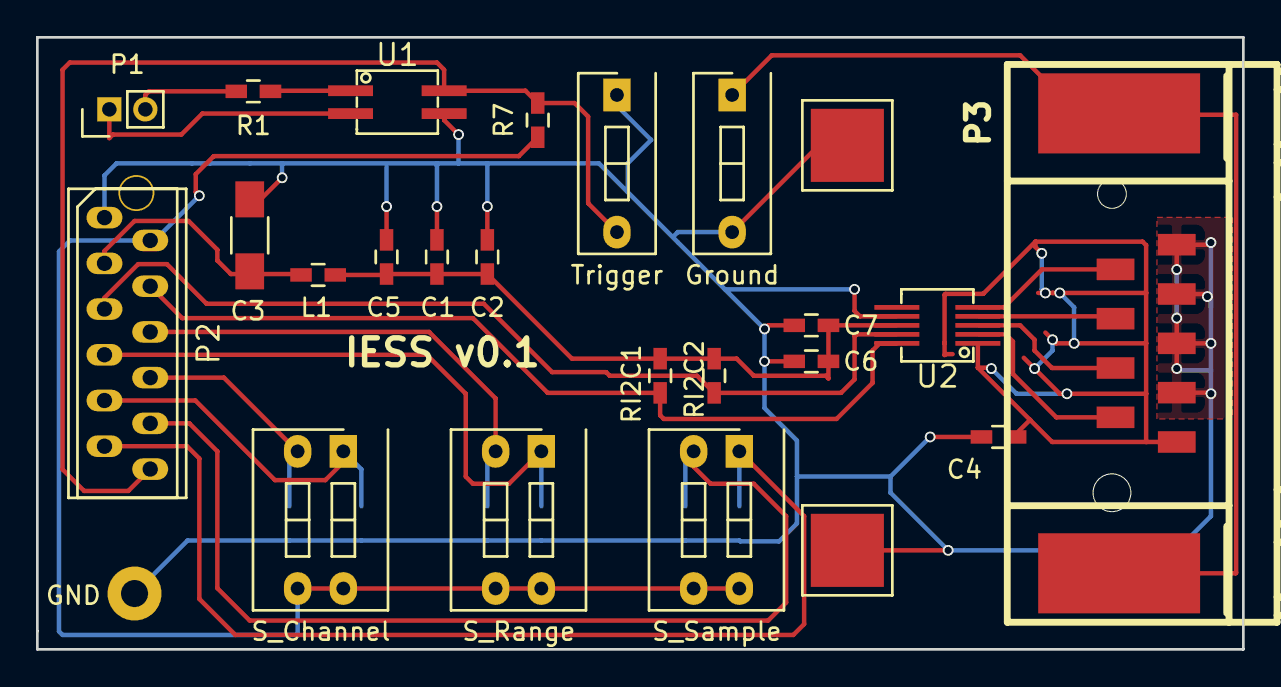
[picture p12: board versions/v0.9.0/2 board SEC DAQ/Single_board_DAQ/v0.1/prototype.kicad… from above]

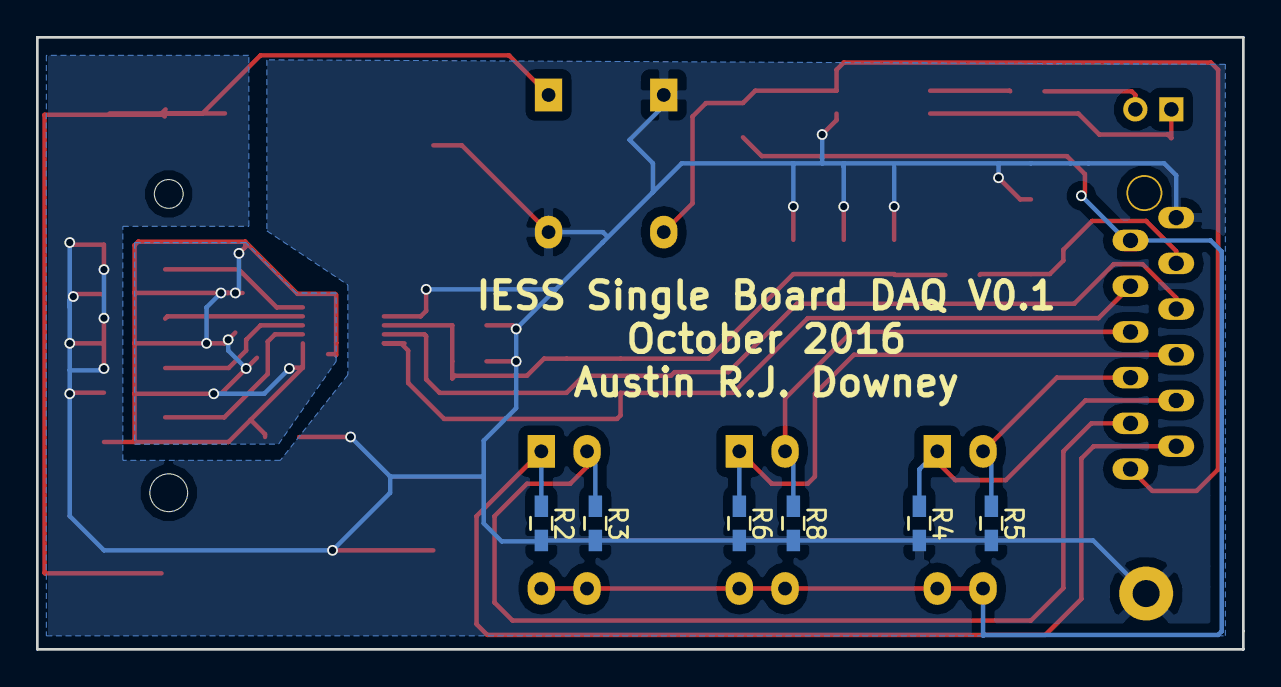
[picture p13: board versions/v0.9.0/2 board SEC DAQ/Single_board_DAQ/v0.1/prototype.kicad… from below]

Board: 2 copper layers, 67.0 x 34.0 mm, 31 parts (6 on the bottom side), 21 nets.

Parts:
C1, C6: 1uF; C_0603_HandSoldering
C2, C7: 0.1uF; C_0603_HandSoldering
C3: 100uF; C_1206_HandSoldering
C4: 51pF; C_0603_HandSoldering
C5: 10uF; C_0603_HandSoldering
GND: TEST_1P; Measurement_Point_Round-TH_Big
Ground: DIPS_01; SW_DIP_x1_Slide
L1: 1uH; C_0603_HandSoldering
P1: CONN_01X02; Pin_Header_Straight_1x02_Pitch2.00mm
P2: CONN_01X12; 3M_12POS_ribbon_conn
P3: P3; SMD_DSUB_9_female
P4, P5: CONN_01X01; 1Pin
R1: 0k1; C_0603_HandSoldering
R2, R3, R4, R5, R6, R7, R8: 10k; C_0603_HandSoldering
RI2C1, RI2C2: 4k7; C_0603_HandSoldering
S_Channel: DIPS_02; SW_DIP_x2_Slide
S_Range: DIPS_02; SW_DIP_x2_Slide
S_Sample: DIPS_02; SW_DIP_x2_Slide
Trigger: DIPS_01; SW_DIP_x1_Slide
U1: EL3H7
U2: FDC1004custom; SOIC_10_FDC1004

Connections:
+3V3: C1.1, C2.1, C3.1, C5.1, C6.1, C7.1, L1.1, L1.2, P2.3, RI2C1.1, RI2C2.1, U2.8
+5V: P2.2, R7.1, S_Channel.3, S_Channel.4, S_Range.3, S_Range.4, S_Sample.3, S_Sample.4
GNDA: C1.2, C2.2, C3.2, C4.2, C5.2, C6.2, C7.2, GND.1, Ground.2, P2.1, P3.1, P3.3, P3.5, P3.7, P4.1, P5.1, R2.2, R3.2, R4.2, R5.2, R6.2, R8.2, Trigger.1, U1.3, U2.7
unnamed: C4.1, P3.9, U2.1
unnamed: P1.1, U1.2
unnamed: P1.2, R1.2
unnamed: P2.6, R8.1, S_Range.2
unnamed: P2.7, R6.1, S_Range.1
unnamed: P2.8, R5.1, S_Channel.2
unnamed: P2.9, R4.1, S_Channel.1
unnamed: P2.10, R3.1, S_Sample.2
unnamed: P2.11, R2.1, S_Sample.1
unnamed: P3.2, U2.5
unnamed: P3.4, U2.4
unnamed: P3.6, U2.3
unnamed: P3.8, U2.2
unnamed: Ground.1, P3.10
unnamed: R1.1, U1.1
SCL: P2.5, RI2C2.2, U2.9
SDA: P2.4, RI2C1.2, U2.10
trigger: P2.12, R7.2, Trigger.2, U1.4

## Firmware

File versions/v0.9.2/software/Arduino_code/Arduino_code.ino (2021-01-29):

// Ausitn Downey
// Feb. 6 - 2017
// Arduino IDE 1.8.1

/*
   FDC 1004 CDC DAQ measure the capacitance of the SEC sensors.
   This code is programed through the switches on the DAQ board
   Updated March 3rd, 2017
   Austin R.J. Downey
   HAVE FUN!!!!!
*/

#include <Wire.h>

// I2C buss address for the FDC1004 used
int FDC = B1010000;

// Address used in the FDC1004 for the FDC Configuration Register, used for triggering and setting the measurment channel
byte FDC_CONFIG = 0x0C;

// Varaibles used is setting the cap offset to the measurment registers
int CapDAC;
int ConfigRegLow;
int ConfigRegHigh;

// build a time stamp
unsigned long SampleTime; // used to obtain a time stamp.
float TimeStamp; // float version of the micro time stamp converted to seconds for the output

// define the digital input pin locations
int range_0 = 3;
int range_1 = 2;
int channel_0 = 5;
int channel_1 = 4;
int sample_0 = 7;
int sample_1 = 6;
int trigger = 8;

// define the variables for the input pins, start as zero
byte val_range = 0;
byte val_channel = 0;
byte val_sample = 0;
int val_catch = 0;

// define and set the offset and sample speed as default incase of a switch fault
int CapOffset = 25;
int SampleSpeed = 100;

// Regesiter values for the Capacitance to Digital Configuration regester, located at 0x0C,
byte RegisterValue1 = B00001100;    // 100 S/s = B00000100; 200 S/s = B00001000; 400 S/s = B00001100;
byte RegisterValueCh1 = B10000000;
byte RegisterValueCh2 = B01000000;
byte RegisterValueCh3 = B00100000;
byte RegisterValueCh4 = B00010000;

//  Sets all channels to positive input channel to the correct input line, and sets the negatice input channel capacitive
//  to digital converter to CAPDAC.
// Sets the Measurement Configuration Registers values to the correct values.  This does channel 1.
byte Ch1Register = 0x08;
byte Ch1Byte1 = B00010000;
byte Ch1Byte2 = B00000000;

// Sets the Measurement Configuration Registers values to the correct register.  This does channel 2.
byte Ch2Register = 0x09;
byte Ch2Byte1 = B00110000;
byte Ch2Byte2 = B00000000;

// Sets the Measurement Configuration Registers values to the correct register.  This does channel 3.
byte Ch3Register = 0x0A;
byte Ch3Byte1 = B01010000;
byte Ch3Byte2 = B00000000;

// Sets the Measurement Configuration Registers values to the correct register.  This does channel 4.
byte Ch4Register = 0x0B;
byte Ch4Byte1 = B01110000;
byte Ch4Byte2 = B00000000;

void setup()
{
  // open the serial port at the correct baud rate.
  Serial.begin(115200);
  Wire.begin(); //initialize the wire libary, Join the bus as master.
  Wire.setClock(400000L); //Optional - set I2C SCL to High Speed Mode of 400kHz.  Run baby run!!


  //sets all the digital pins as inputs and reads the values
  pinMode(range_0, INPUT);
  pinMode(range_1, INPUT);
  pinMode(channel_0, INPUT);
  pinMode(channel_1, INPUT);
  pinMode(sample_0, INPUT);
  pinMode(sample_1, INPUT);
  pinMode(trigger, INPUT);

  // Read the data inputs from the binary switches
  val_range = BinaryThing(range_0, range_1);
  val_channel = BinaryThing(channel_0, channel_1);
  val_sample = BinaryThing(sample_0, sample_1);
  delay(1); // for good measure


  // set the input offset
  if (val_range == 0)
  {
    CapOffset = 30;
  }
  else if (val_range == 1)
  {
    CapOffset = 50;
  }
  else if (val_range == 2)
  {
    CapOffset = 70;
  }
  else if (val_range == 3)
  {
    CapOffset = 90;
  }

  // set the sample speed
  if (val_sample == 0)
  {
    SampleSpeed = 100;
    RegisterValue1 = B00000100;  // 100 S/s = B00000100; 200 S/s = B00001000; 400 S/s = B00001100;
  }
  else if (val_sample == 1)
  {
    SampleSpeed = 200;
    RegisterValue1 = B00001000;
  }
  else if (val_sample == 2)
  {
    SampleSpeed = 400;
    RegisterValue1 = B00001100;
  }
  else if (val_sample == 3)
  {
    SampleSpeed = 400;
    RegisterValue1 = B00001100;
  }


  // set the capoffset
  CapDAC = CapOffset / 3.125; // convert the pF value to the interger for a single sided capacitance measurment
  CapDAC = CapDAC << 5; // shift the set value four to the left to allow for 0s in bits 0:4

  // split the capDAC value into low and high bite, to feen into the registor values
  ConfigRegLow  =  lowByte(CapDAC);
  ConfigRegHigh =  highByte(CapDAC);

  //Combine the CapDAC offset with the channal assingment for the capacitance measurment channel using a bitwise OR statment
  Ch1Byte1 = Ch1Byte1 | ConfigRegHigh;
  Ch2Byte1 = Ch2Byte1 | ConfigRegHigh;
  Ch3Byte1 = Ch3Byte1 | ConfigRegHigh;
  Ch4Byte1 = Ch4Byte1 | ConfigRegHigh;

  // set the low bit to the channel byte 2.  The channels are seperate varaibles incase I ever want a diffrent capdac for each channel
  Ch1Byte2 = ConfigRegLow;
  Ch2Byte2 = ConfigRegLow;
  Ch3Byte2 = ConfigRegLow;
  Ch4Byte2 = ConfigRegLow;

  // write the channel config values ot the channel spefic regieters. i.e. (0x08, 0x09, 0x0A, 0x0B)
  Config(Ch1Register, Ch1Byte1, Ch1Byte2);
  Config(Ch2Register, Ch2Byte1, Ch2Byte2);
  Config(Ch3Register, Ch3Byte1, Ch3Byte2);
  Config(Ch4Register, Ch4Byte1, Ch4Byte2);

}  // end setup

void loop()
{
  // initialize the variables for the loop code
  long Data1, Data2, Data3, Data4;
  float CapCh1, CapCh2, CapCh3, CapCh4;

  // check the trigger lacth and stopp till trigger catch is off
  val_catch = digitalRead(trigger);
  
  while (val_catch == 1)
  {
    delay(1);
    val_catch = digitalRead(trigger);
  }

  // 1 channel measurment
  if (val_channel == 0)
  {
    SampleTime = micros();   // gets the arduino time in microseconds.
    TimeStamp = (((float)SampleTime) / 1000000);

    //Configure the channel 2 sample
    Config(FDC_CONFIG, RegisterValue1, RegisterValueCh1);
    waitData(1);  // pass the channel (1-4) to the wait command  Could use a large delay but this helps to speed up the code//
    Data1 = getdata(0x00);

    // Change the data taken from the FDC from a signed 24 bit number with bits[0-7] = 0 to a unsigned long without the byte of zeros.
    long tempdata1 = SetZero(Data1);

    CapCh1 = (((float) tempdata1) / 524288 ) + CapOffset - 16; // changes data to capacitance.  could remove to speed up code.

    String dataOutput = String(String(TimeStamp,5) + "\t" + String(CapCh1,5));
    Serial.println(dataOutput);
  }

  // 2 channel measurment
  if (val_channel == 1)
  {
    SampleTime = micros();   // gets the arduino time in microseconds.
    TimeStamp = (((float)SampleTime) / 1000000);

    //Configure the channel 2 sample
    Config(FDC_CONFIG, RegisterValue1, RegisterValueCh1);
    waitData(1);  // pass the channel (1-4) to the wait command  Could use a large delay but this helps to speed up the code//
    Data1 = getdata(0x00);

    //Configure the channel 2 sample
    Config(FDC_CONFIG, RegisterValue1, RegisterValueCh2);
    waitData(2);  // pass the channel (1-4) to the wait command  Could use
    Data2 = getdata(0x02);

    // Change the data taken from the FDC from a signed 24 bit number with bits[0-7] = 0 to a unsigned long without the byte of zeros.
    long tempdata1 = SetZero(Data1);
    long tempdata2 = SetZero(Data2);

    CapCh1 = (((float) tempdata1) / 524288 ) + CapOffset - 16; // changes data to capacitance.  could remove to speed up code.
    CapCh2 = (((float) tempdata2) / 524288 ) + CapOffset - 16;

    String dataOutput = String(String(TimeStamp,5) + "\t" + String(CapCh1,5) + "\t" + String(CapCh2,5));
    Serial.println(dataOutput);
  }

  // 3 channel measurment
  if (val_channel == 2)
  {
    SampleTime = micros();   // gets the arduino time in microseconds.
    TimeStamp = (((float)SampleTime) / 1000000);

    //Configure the channel 2 sample
    Config(FDC_CONFIG, RegisterValue1, RegisterValueCh1);
    waitData(1);  // pass the channel (1-4) to the wait command  Could use a large delay but this helps to speed up the code//
    Data1 = getdata(0x00);

    //Configure the channel 2 sample
    Config(FDC_CONFIG, RegisterValue1, RegisterValueCh2);
    waitData(2);  // pass the channel (1-4) to the wait command  Could use
    Data2 = getdata(0x02);

    //Configure the channel 3 sample
    Config(FDC_CONFIG, RegisterValue1, RegisterValueCh3);
    waitData(3);  // pass the channel (1-4) to the wait command  Could use
    Data3 = getdata(0x04);

    // Change the data taken from the FDC from a signed 24 bit number with bits[0-7] = 0 to a unsigned long without the byte of zeros.
    long tempdata1 = SetZero(Data1);
    long tempdata2 = SetZero(Data2);
    long tempdata3 = SetZero(Data3);

    CapCh1 = (((float) tempdata1) / 524288 ) + CapOffset - 16; // changes data to capacitance.  could remove to speed up code.
    CapCh2 = (((float) tempdata2) / 524288 ) + CapOffset - 16;
    CapCh3 = (((float) tempdata3) / 524288 ) + CapOffset - 16;

    String dataOutput = String(String(TimeStamp,5) + "\t" + String(CapCh1,5) + "\t" + String(CapCh2,5) + "\t" + String(CapCh3,5));
    Serial.println(dataOutput);
    
  }

  // 4 channel measurment
  if (val_channel == 3)
  {
    SampleTime = micros();   // gets the arduino time in microseconds.
    TimeStamp = (((float)SampleTime) / 1000000);

    //Configure the channel 2 sample
    Config(FDC_CONFIG, RegisterValue1, RegisterValueCh1);
    waitData(1);  // pass the channel (1-4) to the wait command  Could use a large delay but this helps to speed up the code//
    Data1 = getdata(0x00);

    //Configure the channel 2 sample
    Config(FDC_CONFIG, RegisterValue1, RegisterValueCh2);
    waitData(2);  // pass the channel (1-4) to the wait command  Could use
    Data2 = getdata(0x02);

    //Configure the channel 3 sample
    Config(FDC_CONFIG, RegisterValue1, RegisterValueCh3);
    waitData(3);  // pass the channel (1-4) to the wait command  Could use
    Data3 = getdata(0x04);

    //Configure the channel 4 sample
    Config(FDC_CONFIG, RegisterValue1, RegisterValueCh4);
    waitData(4);  // pass the channel (1-4) to the wait command  Could use
    Data4 = getdata(0x06);

    // Change the data taken from the FDC from a signed 24 bit number with bits[0-7] = 0 to a unsigned long without the byte of zeros.
    long tempdata1 = SetZero(Data1);
    long tempdata2 = SetZero(Data2);
    long tempdata3 = SetZero(Data3);
    long tempdata4 = SetZero(Data4);

    CapCh1 = (((float) tempdata1) / 524288 ) + CapOffset - 16; // changes data to capacitance.  could remove to speed up code.
    CapCh2 = (((float) tempdata2) / 524288 ) + CapOffset - 16;
    CapCh3 = (((float) tempdata3) / 524288 ) + CapOffset - 16;
    CapCh4 = (((float) tempdata4) / 524288 ) + CapOffset - 16;

    String dataOutput = String(String(TimeStamp,5) + "\t" + String(CapCh1,5) + "\t" + String(CapCh2,5) + "\t" + String(CapCh3,5) + "\t" + String(CapCh4,5));
    Serial.println(dataOutput);
  }
}

//////////////////////////////////////////////////////////////////////////////////////////////////////////////////////////////////////////////
// Libary Functions

// This function is used for checking if data is in the registor
unsigned int getinfo(byte pointer)
{
  byte a, b;
  unsigned int c;
  Wire.beginTransmission(FDC);
  Wire.write(pointer);
  Wire.endTransmission(false);  // false for repeated start
  Wire.requestFrom(FDC, 2);
  a = Wire.read();
  b = Wire.read();
  c = word(a, b);    // high, low  line added by Koepel.  comment out my code
  return (c);
}

// This function is used for getting data from registor
unsigned long getdata(byte pointer)
{
  unsigned int a, b;
  unsigned long c = 0;
  a = getinfo(pointer);
  b = getinfo(pointer + 1);
  c = a;
  c = c << 16;
  c |= b;
  return (c);
}

// This function is used for configuring the registor for the next sample
void Config(byte addresse, byte val1, byte val2)
{
  Wire.beginTransmission(FDC);
  Wire.write(addresse);
  Wire.write(val1);
  Wire.write(val2);
  Wire.endTransmission();
}
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

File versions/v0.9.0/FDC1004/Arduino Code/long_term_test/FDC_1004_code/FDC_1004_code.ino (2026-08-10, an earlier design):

// Ausitn Downey
// March 19 - 2016
// Arduino IDE 1.6.6

#include <Wire.h>
#include <SPI.h>
#include <SpiRAM.h>
#include <SD.h>
#include "SparkFunHTU21D.h"

//Create an instance of the object
HTU21D myHumidity;

/*
   FDC 1004 CDC shield that is used to measure the capacitance of the SEC sensors.

   The shield reads the CAP with the CDC and then uses some bit operators to “compress” the dynamic range of the
   CDC (24 bit) onto the 16 bit DAC.  This is than passed to the cRIO and read at 15 bits (as we only use 0 – 5V).
   The best way to do this would be to find a way to digitally write to the cRIO

   The best way to use this code is to set the CapOffset to as close to the steady state capacitance for the sensor
   and then set the dynamic range as small as possible (Max 30) as to capture all of the dynamic sampling on the DAC.
   The Dynamic range may not matter if we find a way to shift the FDC results out digitally.

   Set the speed in SampleSpeed, know that 100Hz / 4 Channels will read each sensor at 25Hz.  Add to this the time
   the microcontroller needs the final sample frequency is around .. 13 Hz.

   13 Hz --  100S/s Printing cap and time stamp to Serial at 9600 baud.
   20.5 Hz --  100S/s Printing cap and time stamp to Serial at 250000 baud.
   22.7 Hz --  100S/s Printing time stamp to Serial at 250000 baud.

   The resolution of the FDC1004 depends on the sample speed selected.  Use lower speeds for higher resolution.
   Only the FDC sample speed (100,200,400) should effect the FDC's resolution.


   To use this code with the Arduinos serial port only download CoolTerm form
   http://freeware.the-meiers.org/

   Click the connect button on the top.
   Change the Baud rate to what you select in Coolterm and turn on the time stamp selection from one of the
   drop down menu connection > options.

   connection > options > receive  click the add timestamps to received data

   Collect data under connection > capture to text file

   HAVE FUN!!!!!
*/



// Define varaibles for the code

//////////////////////////////////////////////////////////////////////////////////////
//////////////////////////////////////////////////////////////////////////////////////
int CapOffset = 90;     // Cap offset in Pf. Max of 96 pF.                  //////////
int SampleSpeed = 100;  // set to 100, 200 or 400 S/s                       //////////
int DynamicRange = 30;  //  Set the dynamic sensor range about the DAC      //////////
unsigned int dataCycles = 5000;   // number of data point in a sample       //////////
//////////////////////////////////////////////////////////////////////////////////////
//////////////////////////////////////////////////////////////////////////////////////

// set the pinout for the SRAM
#define SS_PIN 10


// set up the SpiRam clock and Chip select
byte clock = 0;
SpiRAM spiRam(0, SS_PIN);

// set pin 8 as the slave select for the MAX 5134 DAC:  This is harware 10, but is unused in this code
const int CS1 = 8;


/*
    CS - to digital pin 10  (SS pin)
    SDI - to digital pin 11 (MOSI pin)
    CLK - to digital pin 13 (SCK pin)
*/


// I2C buss address for the FDC1004 used
int FDC = B1010000;
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

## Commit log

2021-01-29 initial upload
    [Parts.ods, noname_shell.dsn, prototype.csv, prototype.dsn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]
2021-10-20 cleaned up repo, added figure
    [AMP wires.xlsx, FDC1004_4Ch.fzz, FDC1004_4Ch_contour.gm1, FDC1004_4Ch_copperBottom.gbl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]
